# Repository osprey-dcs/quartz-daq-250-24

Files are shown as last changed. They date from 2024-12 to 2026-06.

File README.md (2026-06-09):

# Osprey Quartz DAQ-250-24

Open Hardware repository for Osprey DCS Quartz DAQ-250-24
distributed ADC chassis.

Revision 2

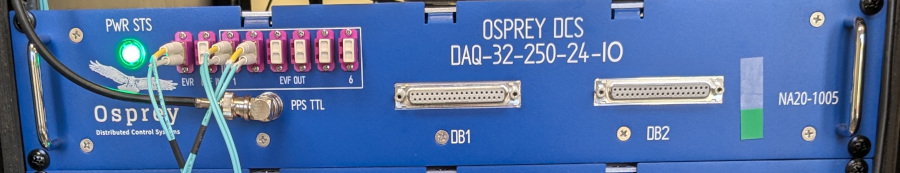
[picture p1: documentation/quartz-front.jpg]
Front panel


## Contents

- [3D model](chassis-rev2.stp.xz) of 2U Chassis, including Marble and Quartz PCBs
- [Bill of materials](chassis-bom-rev2.csv) for chassis assembly.
- [Wiring](chassis-wiring-rev2.kicad_sch) diagram.
- Pre-built [firmware](firmware) images

- Documents
  - Quartz [DAQ-250-24](documentation/quartz-daq-250-24-datasheet.md) datasheet
  - **[Quick-start](documentation/quick-start.md)** Guide
  - [EPICS IOC Setup](documentation/ioc-setup.md)
  - [Acquisition Engine](documentation/acquire.md) setup
  - New [System Setup](documentation/system-setup.md)
  - [Chassis Setup/Recovery](documentation/chassis-setup.md)
  - [New Marble PCB](documentation/marble-bring-up-procedure.pdf) one-time factory bring-up process
  - Quartz bench testing [report](documentation/functional-testing.md)
  - Notes for [RHEL](documentation/rhel-notes.md) derivatives
  - Quartz [file format](https://github.com/osprey-dcs/atf-previewer/blob/main/documentation/file-formats.md)

## Related

- [Marble PCB](https://github.com/BerkeleyLab/Marble) schematic and artwork
- [Marble MMC](https://github.com/BerkeleyLab/Marble-MMC) firmware
- [Marble bootloader](https://github.com/BerkeleyLab/Bedrock) firmware
  - [Alluvium](https://github.com/mdavidsaver/alluvium) remote flash chip access
- [Quartz PCB](https://github.com/osprey-dcs/Quartz) schematic and artwork
- [Quartz application](https://github.com/osprey-dcs/Quartz-firmware) firmware
- [Interlock I/O PCB](https://github.com/osprey-dcs/pmod-mps-io)

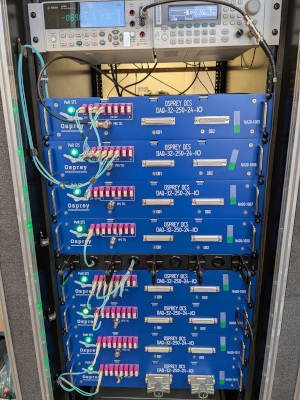
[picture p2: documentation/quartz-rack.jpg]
Installation


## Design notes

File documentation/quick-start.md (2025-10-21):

# Quartz Quickstart Guide

A (somewhat) quick overview of the components and processes for setting up a new Quartz ADC chassis.

## Equipment

* [Electrical](system-setup.md#prerequisites)
* Computing
  * Host for running GUI
  * Linux host for IOCs (no GUI).  May combine.
  * NTPv3 server (may use Linux host)
* Software processes
  * [Quartz IOC](ioc-setup.md#prerequisites) (required)
  * Control System Studio/Phoebus GUI client

## Preparation

* Install [Quartz IOC](ioc-setup.md#prerequisites) and associated software

## Physical

cf. [Single Chassis](system-setup.md#single-chassis) standalone wiring.

1. Unbox and rack up the Quartz chassis
1. Attach ground wire
1. Plug in 12V AC/DC power adapter
1. Connect ethernet
1. Connect pulse-per-second (PPS) input from GPS/GNSS (TTL).
1. [Connect micro-USB](chassis-setup.md#connect-usb) (optional, change IP configuration)

## IP address setup

Initially, the chassis should be directly connected (or on the same subnet)
as the computer used for

1. Apply power to chassis
1. Set [IP and/or MAC addresses](chassis-setup.md#set-ipmac-address)
1. Power cycle chassis
1. Ping test with new IP address
1. Boot chassis to [Application firewmare](ioc-setup.md#ioc-configuration).
   May be done with full IOC, or alluvium CLI.
1. Use Application console to set netmask and gateway.
   For node 1 (EVG) only, also set NTP server address
1. Power cycle or reboot

## Setup IOC

1. Build [Quartz IOC](ioc-setup.md#prerequisites) and dependencies.
1. Edit `iocBoot/iocNASA_ACQ/node01.cmd` with selected [correct IP address](ioc-setup.md#ioc-configuration), then run.
1. Check `FDAS:01:GLD:image` PV

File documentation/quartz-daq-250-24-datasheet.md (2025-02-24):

# Quartz DAQ-250-24 Datasheet

Osprey Quartz is a highly scalable EPICS native 24-bit 250KHz data acquisition system
consisting of one or more 2U 19-inch rack mounted chassis.
Each chassis can digitizer up to 32 channels connected through two standard DB37F connectors.
The input scale is fixed to $\pm 10$ volts with per-channel selectable AC or DC coupling.

Multiple chassis may be [connected together](system-setup.md#Topologies)
which maintaining a common sample clock phase.
This permits synchronous sampling with a very high channel count[^maxchan].

[^maxchan]: There is no hard upper limit on channel count.
  Sample clock synchronization quality degrades as timing network topology deepens.

## Parameters

| Parameter | Value |
| ---- | ---- |
| Height | 2U |
| Width | 19 Inch |
| Depth | 400 mm |
| Communication | 1Gbps Ethernet, RJ45 |
| Power Input Voltage | 12 VDC into 2 contact [DC barrel Jack](#PowerInput)[^acdc] |
| Number of Analog channels | 32 per chassis |
| Analog Input | 2x DB37-F |
| Sample rates | 1K, 5K, 10K, 25K, 50K, 250K samples per second |
| AC/DC coupling | selectable per-channel |
| ADC Resolution | 24-bit |

## Absolute Maximums

| Specification | Minimum | Maximum |
| ---- | ---- | ---- |
| Ambient Temperature | 0 C | 40 C |
| Ambient Humidity | | 90% non-condensing |
| Power Input Voltage[^acdc] | 0V DC | 13 VDC |
| Power Current | | 4A |
| Analog Input abs. voltage[^analogabs] | -15 V | +15 V (DC coupled) |
|                                       | -25 V | +25 V (AC coupled)[^analogabsac] |
| Analog Input diff. voltage[^analogdiff] | -30 V | +30 V |
| Pulse-per-second Input Voltage | -0.7 V | 5.5 V |

[^acdc]: 120V AC/DC converter included.
[^analogabs]: Voltage applied to any DB37 pin with respect to chassis ground.
[^analogabsac]: For frequencies less than the 16 Hz.
[^analogdiff]: Voltage difference between each pair of pins.

## Performance

| Specification | Minimum | Typical | Maximum |
| ---- | ---- | ---- | ---- |
| Power Input Voltage[^acdc] | 10 V | 12 V | 13 V DC |
| Analog Input Impedance | 999k ohm | 1M ohm | |
| Analog Input voltage | -10V | | 10V |
| Analog bandwidth | | | 100KHz @ 250Ksps|
|                  | | |  20KHz @ 50Ksps |
|                  | | |  10KHz @ 20Ksps |
|                  | | |  5KHz @ 10Ksps |
|                  | | |  2KHz @ 5Ksps |
|                  | | |  400Hz @ 1Ksps |
| Channel Cross-talk[^cross] | | | -94 dB |
| Gain Accuracy | | | 0.13 % |
| Pass-band ripple | 0.1 dB | | |
| Effective resolution | | 19 bits @ 250Ksps | |

[^cross]: Worst case of 100KHz measured on an adjacent channel on same side of PCB, sharing the same ADC chip.

## Connectors

- Power Input.

2 contact barrel jack, positive inside.  Cliff Electronics [SCD-026](http://www.farnell.com/datasheets/1859067.pdf)

- Grounding stud

- Ethernet RJ45 UTP

- Timing, 8x LC duplex, multi-mode

- 2x DB37-F

Each DB37-F connector has 16 inputs pairs.

Quartz DB37-F pinout

Board side connector is TE Connectivity [5747847-6](https://www.te.com/commerce/DocumentDelivery/DDEController?Action=showdoc&DocId=Catalog+Section%7F82068_AMPLIMITE_Right-Angle_Posted_Conn%7F0412%7Fpdf%7FEnglish%7FENG_CS_82068_AMPLIMITE_Right-Angle_Posted_Conn_0412.pdf%7F5747847-4)

- Pulse Per Second, BNC-F

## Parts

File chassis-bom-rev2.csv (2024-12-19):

QTY | Part | VENDOR | VENDOR# | Manufacturer | MFN# | Description | NOTE
1 | Fan extension cables | Amazon | Noctua NA-SEC2 | Noctua | NA-SEC2 | Pre terminated fan extension cables 12 in
1 | FGPA heatsink | Coolinnovations | 4-101010P | Coolinnovations | 4-101011P | Splayed Design, Copper Heat Sink | Use adhesive to attach to marble
2 | Fan guard | Digi-Key | 259-1623-ND | Sunon Fans | FG-4 | FAN GUARD 40MM METAL
2 | FAN1, FAN2 | Digi-Key | 259-1844-ND | Sunon Fans | MF40201V1-1000U-G99 | 12VDC Fan, 40 mm x 40 mm x 20mm
3 | Spades for LED+Fuse | Digi-Key | 314-AI-50207-ND | Mueller Electronics | AI-50207 | 0.250" (6.35mm) Quick Connect Female 18-22 AWG Crimp Connector Insulated
1 | Thermal Epoxy | Digi-Key | 473-8349TFM-50ML-ND | MG Chemicals | 8349TFM-50ML | Thermal Epoxy for heatsink | Adhesive for heatsinks
2 | BLK Hook Up Wire | Digi-Key | 5856/7BK005-ND | Alpha Wire | 5856/7 BK005 | HOOK-UP STRND 20AWG BLACK 100' | Wire for internal power
2 | RED Hook Up Wire | Digi-Key | 5856/7RD005-ND | Alpha Wire | 5856/7 RD005 | HOOK-UP STRND 20AWG RED 100' | Wire for internal power
1 | Crimp Tool (Power Connector) | Digi-Key | 58614-1-ND | TE Application Tooling | 58614-1 | TOOL HAND CRIMPER 18-24AWG SIDE
1 | Crimp Tool Die (Power Connector) | Digi-Key | A100343-ND | TE Application Tooling | 58614-2 | Tool Die Set For Rectangular Contacts, 18-24 AWG
2 | J19 Pins | Digi-Key | A19991CT-ND | TE Connectivity | 640252-2 | CONN SOCKET 18-24AWG CRIMP TIN
1 | J19 | Digi-Key | A24111-ND | TE Connectivity | 770849-2 | CONN RCPT HSG 2POS 3.96MM | Marble power connector
1 | SW1 | Digi-Key | EG1889-ND | E-Switch | RR3130ABLKBLKFS | SWITCH ROCKER SPST 10A 125V
1 | F1 | Digi-Key | F013-ND | Littlefuse | 03420838H | FUSE HLDR CART 250V 20A PNL MNT
1 | FUSE | Digi-Key | F1769-ND | Littelfuse Inc. | 0313005.MXP | FUSE GLASS 5A 250VAC 3AB 3AG
1 | Power Plug | Digi-Key | GSM60U12-P1J | Mean Well USA | 1866-5524-ND | AC/DC WALL MOUNT ADAPTER 12V 54W | Wall wort
2 | 2U Chassis Handles (comes with screws) | Digi-Key | HM1269-ND | Hammond Manufacturing | 1427Q | HANDLE STL/CHROME MTG CTR 2.299" | Handles
2 | JX-M1, JX-M2, 3 Pin Connector (Fan Cable) | Digi-Key | S9434-ND | Sullins Connector Solutions | SWH25X-NULC-S03-UU-BA | 3 Rectangular Connectors - Housings Receptacle Beige 0.100" (2.54mm) | Fan connector
6 | 3 Pin Connector Pins (Fan Cable) | Digi-Key | S9473TR-ND | Sullins Connector Solutions | SWT25X-URTC-S01-UU-UU | Socket Contact Tin 20-26 AWG Crimp - | Fan connector pins
1 | Ethernet | Digikey | 1195-3540-ND | HARTING | 9454521504 | CABLE MOD 8P8C JACK-PLUG 1.64'
1 | 12 VDC LED | Digikey | 350-4318-ND | Dialight | 655-1203-104F | LED PANEL INDICATOR GREEN 12V
1 | BNC to SMA Cable | Digikey | 3985-PE3733LF-12-ND | Pasternack | 3985-PE3733LF-12-ND | 12 inch BNC to SMA internal chassis cable
1 | Micro USB | Firewire | RR-MCBR-EXTPM-12GX5 | Firewire | RR-MCBR-EXTPM-12GX5 | Right angle micro usb cable
8 | LC Panelmount adapter | FS | FH-LCU-DXF-OM4 | FS | FH-LCU-DXF-OM4 | LC/UPC to LC/UPC Duplex OM4 Multimode SC Footprint Plastic Fiber Optic Adapter/Coupler with Flange
2 | SFP breakout cable | FS | FMTPLCOM4 | FS | FMTPLCOM4 | 1m (3ft) MTP® Female to 4 LC UPC Duplex 8 Fibers Type B Plenum (OFNP) OM4 50/125
2 | QSFP Adapater | FS | QSFP-SR4-40G | FS | QSFP-SR4-40G | Generic QSFP-SR4-40G Compatible 40GBASE-SR4 QSFP+
16 | nut for LC conenctors | McmasterCarr | 90592A075 | McmasterCarr | 90592A075 | Steel Hex Nut Class 8, M2 x 0.4 mm Thread | LC connector
8 | M4 Hex Nut, 100 Pack (fans) | McmasterCarr | 90710A035 | McmasterCarr | 90710A035 | 18-8 Stainless Steel Thin Hex Nut M4 x 0.7 mm Thread, DIN 439B, ISO 4035 | For fans
8 | Socket Head Screw M4 x 0.7 mm Thread, 30 mm Long (fans) | McmasterCarr | 91292A130 | McmasterCarr | 91292A130 | 18-8 Stainless Steel Socket Head Screw M4 x 0.7 mm Thread, 30 mm Long | For fans
16 | screw for LC connectors | McmasterCarr | 92000A017 | McmasterCarr | 92000A017 | Passivated 18-8 Stainless Steel Pan Head Phillips Screws M2 x 0.4mm Thread, 10mm Long | LC connector
15 | M2.5x0.45 Pan Head Phillips Screws (Marble+Quartz) | McmasterCarr | 92000A105 | McmasterCarr | 92000A105 | Passivated 18-8 Stainless Steel Pan Head Phillips Screws M2.5 x 0.45mm Thread, 8mm Long | Marble
16 | M4 Split Washer, 100 Pack (fans) | McmasterCarr | 92148A160 | McmasterCarr | 92148A160 | 18-8 Stainless Steel Split Lock Washer for M4 Screw Size, Standard, 4.4 mm ID | For fans
4 | Jack screw between Marble and Quartz | McmasterCarr | 93655A096 | McmasterCarr | 93655A096 | Male-Female Threaded Hex Standoff 4.500 mm Hex, 10 mm Long, M2.5 x 0.45 mm Thread
1 | Grounding wire | McmasterCarr | https://www.mcmaster.com/6981T6-6981T695/ | McmasterCarr | 6981T6 | Grounding wire to connect chassis to GND bar 500ft | GND
2 | Grounding lug | McmasterCarr | https://www.mcmaster.com/7113K455/ | McmasterCarr | 7113K455 | Ring terminal for GND 14-16 awg No10 screw | GND
1 | Grounding nut (chassis | McmasterCarr | https://www.mcmaster.com/91240A009/ | McmasterCarr | 91240A009 | 8-32 stainless steel nut | GND
1 | Grounding nut (GND bar) | McmasterCarr | https://www.mcmaster.com/91240A411/ | McmasterCarr | 91240A411 | 10-32 stainless steel nut | GND
1 | Grounding Screw | McmasterCarr | https://www.mcmaster.com/92597A140/ | McmasterCarr | 92597A140 | Grounding screw for GND bar 10-32 3/4in (pack of 25) | GND
3 | 19mm standoff for quartz | McmasterCarr | https://www.mcmaster.com/94868A173/ | McmasterCarr | 94868A173 | 19mm hex standoff 2.5M partially threaded | Quartz standoff
4 | Star washers | McmasterCarr | https://www.mcmaster.com/97775A521/ | McmasterCarr | 97775A521 | Star washers for grounding chassis and bar | GND
2 | 2.5M washers for Quartz standoffs | McmasterCarr | https://www.mcmaster.com/98689A111/ | McmasterCarr | 98689A111 | Pack of 100 2.5M washers | Quartz standoff
1 | BNC | Newark | 07H2407 | LCOM | BA1087 | Adapter Coaxial Connector BNC Jack, Female Socket To BNC Jack, Female Socket 50 Ohms
1 | PG1 | Newark | 94X0659 | Cliff Electronic Components | FC681445 | DC Power Connector, Jack, 2.1 mm, Panel Mount, Solder | Power plug
1 | Fan Filter | PPCS | MDY-FF-PVC-4 | PPCS | MDY-FF-PVC-4 | Ultra Thin 0.45mm PVC Fan Dust Filter - 4cm
1 | Marble Chassis | Protocase |  |  |  | 2U custom chassis frame built to house related components. Hardware Included. | Chassis Shell
16 | 8-32 countersunk screw | Protocase Supplied
16 | 8-32 PemNut | Protocase Supplied
6 | 8-32 stud | Protocase Supplied
6 | 8-32 nut | Protocase Supplied
12 | M2.5 PEM Standoffs 10mm | Protocase Supplied
2 | M2.5 PEM Stanoffs 19mm | Protocase Supplied
1 | Marble Board | Osprey DCS
1 | Quartz Board | Osprey DCS

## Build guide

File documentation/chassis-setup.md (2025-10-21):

# Quartz Chassis Setup and Recovery

This document describes a process to discover or set
the unique identifiers and firmware of a Quartz
digitizer chassis with unknown configuration.

This process consists of the following tasks:

1. Update application firmware
1. Set IP and MAC addresses
1. Completely reprogram flash chip (not recommended for end user)

## Prerequisites

1. Working Debian Linux 12 computer with internet access.
2. Quartz-DAQ-250-24 chassis
  - Marble 1.4.1 PCB
  - Quartz 1.x PCB (serial numbers less than 200)
3. Micro-USB cable
4. Fine point non-conductive stylus to operate micro-switch

## Preparation

```sh
# procedure tested with OpenOCD 0.12.0, pyserial 3.5
sudo apt-get install openocd python3-serial git

git clone https://github.com/mdavidsaver/alluvium.git
```

Download [marble.cfg](https://github.com/BerkeleyLab/Bedrock/blob/06b84d9ba8c3c41bc6aa823fadfbee9f15dfdd08/board_support/marblemini/marble.cfg#L2) or the [local copy](firmware/marble.cfg).

Download a [bootloader firmware](../firmware/marble-bootloader/) image file.

Download an [application firmware](../firmware/quartz-application/) image file.

## Program Application Firmware

The application firmware may be loaded while the bootloader firmware is running
via the alluvium utility.

```sh
$ cd alluvium
$ python3 -m alluvium 192.168.79.8 clear
$ python3 -m alluvium 192.168.79.8 erase app 8m
$ python3 -m alluvium 192.168.79.8 program app quartzV1-20241230-350d71f.bit
```

## Connect USB

Note: connecting the micro USB port will supply 3.3V power to an on-board FTDI USB to serial chip!
This may safely by done before or after connecting the main 12V power.
For the purposes of this document, connect the USB first in order to see output printed during MMC boot.

Depending on Quartz chassis revision, either plug into the front panel
USB port, or remove chassis lid and look for the USB pigtail port.

The micro USB connection on a Marble V1 PCB provides four virtual serial ports,
which will always appear in this relative order.

1. FPGA JTAG
2. Unused
3. FPGA debug UART
4. Management Microcontroller (MMC) UART

These will typically appear as `/dev/ttyUSB0` through `/dev/ttyUSB3`.
However, if eg. the host already has `/dev/ttyUSB0` for another device,
then they will appear as ttyUSB1 through ttyUSB3.
Assuming enumeration as 0 through 3, access the MMC console.

```sh
$ python -m serial.tools.miniterm /dev/ttyUSB3 115200
--- Miniterm on /dev/ttyUSB3  115200,8,N,1 ---
--- Quit: Ctrl+] | Menu: Ctrl+T | Help: Ctrl+T followed by Ctrl+H ---
```

Now switch on the chassis.  During the boot process the current
IP and MAC addresses will be printed.

## Set IP/MAC Address

The IP and MAC addresses may be changed via the MMC UART console.

While connected to the MMC UART, press `?` then Return to print a list of commands.

```
hardware board id 0x12

Build based on git commit 86a9bf22
Menu:
1 - MDIO/PHY
...
m d.d.d.d - Set IP Address
n d:d:d:d:d:d - Set MAC Address
...
```

The `m` and `n` commands will set/overwrite the addresses.

Quartz chassis are shipped with IP and MAC of the forms: `192.168.79.ddd` and `12:55:55:00:1f:XX`
where `ddd` and `XX` are the Marble PCB serial number in decimal and hexadecimal respectively.
eg. for Marble S/N 8.

```
m 192.168.79.8
n 12:55:55:00:1f:08
```

Note: there is no setting for network mask (netmask) or default gateway through the MMC console
as these are not necessary for LEEP traffic (device only replies to sender).
Network mask and gateway are separately configured for the Quartz application fireware,
for use by the NTP client.

### Verify Communication

After changing the IP address, power cycle the chassis and attempt to ping.

Note: the bootloader firmware will respond to a ping (ICMP), the application firmware will not.
      So for this test first stop any Quartz IOC from communication with the chassis.

Either firmware will respond to ARP requests.
So after attempting a `ping`, also check the ARP cache.

A positive result will show a MAC address (aka. Link Layer ADDRess):

```sh
$ ip neigh
...
192.168.79.7 dev eth0 lladdr 12:55:55:00:1f:07 REACHABLE
```

A negative result will not:

```sh
$ ip neigh
...
192.168.79.90 dev eth0 INCOMPLETE
```

The bootloader firmware may also be used with the `alluvium` tool.

```
$ cd alluvium
$ python3 -m alluvium 192.168.79.8 status
SR1 0b10011000 [SRWD  , p_err , e_err , BP2   , BP1   , bp0   , wel   , wip   ]
SR2 0b00000000 [es   , ps   ]
CR1 0b00100100 [lc1   , lc0   , TBPROT, dnu, bpnv  , TBPARM, quad  , freeze]
```

## Re-program Flash Chip

**Do not perform the following unless specifically directed to do so.**

## Overwrite FPGA bootloader image

As shipped, the 16MB flash chip on a Marble is partitioned into two 8MB sections
referred to as `gold` (lower) and `app` (upper).
The upper `app` section may be overwritten remotely at will.
The lower `gold` section is not writable without physical access to a chassis.

The following is **not necessary** to program the application image!

See for technical details on [flash chip write protections](https://github.com/mdavidsaver/alluvium/blob/master/marble-protect.md).

### Disable all flash write protections

1. Power off chassis
2. Toggle SW1 closed (tab towards QSFP cage)
3. Load the bootloader bit file into FPGA RAM

Run the following, replacing `/home/user/golden-1.4.1-b8ea502.bit` with the path
to the actual path to the file downloaded earlier.

Note: openocd does not expand tilda (`~`) in path names.

```sh
openocd -f marble.cfg -c 'transport select jtag; init; xc7_program xc7.tap; pld load 0 /home/user/golden-1.4.1-b8ea502.bit; exit'
```

Success exits with zero and output ends with

```
Info : JTAG tap: xc7.tap tap/device found: 0x0364c093 (mfg: 0x049 (Xilinx), part: 0x364c, ver: 0x0)
```

Unsuccessful has a non-zero exit code with an error like:

```
Error: couldn't stat() ~/golden-1.4.1-b8ea502.bit: No such file or directory
failed loading file ~/golden-1.4.1-b8ea502.bit to pld device 0
```

Also see the "libusb permissions" section below.

On success the FPGA is now running the golden/bootloader firmware,
which will be used to program the flash chip.

4. Zero the SR1 register

This step will fail unless SW1 is closed (see above)

```sh
python3 -m alluvium 192.168.79.8 clear
python3 -m alluvium 192.168.79.8 setup --sr1 0
```

Note: `clear` in this context clears flash chip error status,
      and does not alter the contents.

5. Optional, backup flash contents

```sh
# Optional
python3 -m alluvium 192.168.79.8 read 0 16M -f backup.bin
```

This backup may be restored with:

```sh
# Optional
python3 -m alluvium 192.168.79.8 program 0 backup.bin
```

6. Bulk erase

The following will erase the entire flash chip.

```sh
# Erases entire flash!!
python3 -m alluvium 192.168.79.8 wipe
```

7. Program bootloader firmware

Write the same firmware image file to the lower part of the flash.

```sh
python3 -m alluvium 192.168.79.8 program gold /home/user/golden-1.4.1-b8ea502.bit
```

8. Optional, verify

Power cycle the chassis and re-run:

```sh
python3 -m alluvium 192.168.79.8 clear
```

9. Restore write protections

```sh
python3 -m alluvium 192.168.79.8 clear
python3 -m alluvium 192.168.79.8 setup --sr1 0b10011000
```

10. Power off chassis
11. Toggle SW1 open (tab away from QSFP cage)

12. Optional, verify

The following commands will now fail.

```sh
python3 -m alluvium 192.168.79.8 setup --sr1 0

python3 -m alluvium 192.168.79.8 erase gold 8M
```

### libusb permissions

`openocd` errors like the following indicate that the user account does not have permission
to access the USB device.

```
Error: libusb_open() failed with LIBUSB_ERROR_ACCESS
Error: no device found
Error: unable to open ftdi device with vid 0403, pid 6011, description '*', serial '*' at bus location '*'
```

Either run as super-user or location change change
the permissions of the appropriate `/dev` file.

```sh
$ lsusb
Bus 001 Device 005: ID 0403:6011 Future Technology Devices International, Ltd FT4232H Quad HS USB-UART/FIFO IC
...
$ ls -l /dev/bus/usb/001/005
crw-rw---- 1 root plugdev 189, 4 Feb 15 08:39 /dev/bus/usb/001/005
$ sudo chmod a+rw /dev/bus/usb/001/005
```

## Quartz EEPROM

The Quartz PCB includes an EEPROM which holds FMC meta-data,
including manufacturer, product, and serial number in the
[FRU](https://www.intel.com/content/www/us/en/servers/ipmi/information-storage-definition.html)
(Field Replaceable Unit) format.

The [frugy](https://pypi.org/project/frugy/) tool can produce EEPROM images
using configuration files present in the
[Quartz](https://github.com/osprey-dcs/Quartz/tree/quartz-1.x/Documentation/EEPROM) repository.

```sh
sudo apt-get install python3-virtualenv atftp

git clone --branch quartz-1.x https://github.com/osprey-dcs/Quartz
cd Documentation/EEPROM

virtualenv /tmp/fruenv
. /tmp/fruenv/bin/activate
pip install frugy
```

Now create EEPROM image, and attempt to program and verify, serial number 256 (IP address `192.168.79.256`).

Substitute actual board variant and serial number.

```sh
./createEEPROM.sh QuartzEEPROM-v1.2.2.yml 256
```

When writing the EEPROM, the J6 jumper on Quartz must be **closed/shorted**.

The current contents may be read with:

```sh
atftp --get -l EEPROM_rb.bin -r FMC1_EEPROM.bin 192.168.79.256
```

And manually written confirmed with:

```sh
atftp --put -l EEPROM_010.bin -r FMC1_EEPROM.bin 192.168.79.256
atftp --get -l EEPROM_rb.bin -r FMC1_EEPROM.bin 192.168.79.256
diff EEPROM_010.bin EEPROM_rb.bin
```

It is strongly recommended to always read back and compare after writing to the EEPROM.

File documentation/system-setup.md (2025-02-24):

# Quartz ADC System Setup

This document describes setting up a new Quartz installation.

## Prerequisites

1. One or more Quartz ADC chassis
  - One 12V power supply for each
  - Ground connection (essential for measurement accuracy!)
2. Time server with 5V TTL PPS output
  - Either a dedicated ethernet enabled GPS receiver with NTP server
  - Another GPS receiver with 5V TTL PPS output, and a separate NTP server
3. Cables
  - cable to BNC-F on one Quartz chassis from time server (PPS)
  - LC duplex fiber patch cables
    - At least one is required to test a single chassis
  - Ethernet cable(s) to computer
4. Working Debian Linux 12 computer with internet access.

## EVG / Timing Master Node

In each installation, one chassis must be selected as a "master" node for the timing network.
This node will connect to the time server via. ethernet and pulse-per-second inputs and
provide timing and synchronization for all other chassis.

Any chassis may act as a "master" node.
This selection is made by configuring the NTP server through the
[application firmware console](ioc-setup.md#fpga-application-console).

### Time Server Setup

For production installations, a dedicated time server with GPS input, NTP server, and PPS output is recommended.

Alternately, for testing and development, the following parts may be assembled to provided a suitable
PPS, along with a software NTP server.

- [GPS GNSS with USB](https://www.adafruit.com/product/4279)
- [SMA to uFL adapter](https://www.adafruit.com/product/851)
- [GPS Antenna - External Active](https://www.adafruit.com/product/960)
- [BNC Male Plug Terminal Block](https://www.adafruit.com/product/2888)
- Suitable wire, soldering iron, and a steady hand.

## Connections

Summary of Quartz chassis connectors referenced below

- Fiber (LC)
  - Port 1 - EVR IN
  - Port 2 - EVG IN
  - Ports 3 -> 8 - EVF OUT
- PPS TTL (BNC)

## Topologies

### Single chassis

The minimal connections required to run a single chassis are:

- Port 3 -> Port 1
- Time server PPS output -> PPS TTL
- Ethernet connection between chassis, computer, and NTP server

Single chassis

### Up to 6 chassis

Up to 5 more chassis may be connected from Ports 4 through 8 on the "master" node
to EVR IN on each secondary node.

Six chassis

### 7 to 32 chassis

With more than six chassis, it is necessary to add tertiary (level 3) nodes from
one or more secondary (level 2) nodes.

32 chassis

Here each Level 2 node will connect to itself, and up to 5 other Level 3 nodes.

This arrangement require an alteration to the "master" node, which will no longer
be looped directly to itself.
Instead, the "master" node will be connected to itself through one of the level 2 nodes.

This maintains an equal propagation time from from the Ports 3 -> 8 on the "master"
node, and the Port 1's on each node (including the master).

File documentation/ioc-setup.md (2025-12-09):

# Quartz EPICS IOC Setup

This document describes setting up and running an EPICS IOC
to communicate with a Quartz ADC chassis

## Prerequisites

1. Working Debian Linux 12 computer with internet access.
2. Quartz-DAQ-250-24 chassis
  - IP address known.
  - This document uses `192.168.79.8` as an example
  - Application firmware image programmed
3. (Optional) Installation of cs-studio phoebus GUI

## Preparation

```sh
sudo apt-get update
sudo apt-get install -y build-essential git libevent-dev libz-dev libfftw3-dev libreadline-dev python3 python3-serial python-is-python3
```

```sh
git clone --branch 7.0 https://github.com/epics-base/epics-base
git clone --branch master https://github.com/epics-base/pvxs
git clone --branch master https://github.com/epics-modules/autosave
git clone --branch master https://github.com/osprey-dcs/feed-core
git clone --branch master https://github.com/osprey-dcs/pscdrv
git clone --branch main https://github.com/osprey-dcs/atf-acq-ioc
git clone https://github.com/mdavidsaver/alluvium

cat <<EOF > pvxs/configure/RELEASE.local
EPICS_BASE=\$(TOP)/../epics-base
EOF

cat <<EOF > autosave/configure/RELEASE.local
EPICS_BASE=\$(TOP)/../epics-base
EOF

cat <<EOF > feed-core/configure/RELEASE.local
EPICS_BASE=\$(TOP)/../epics-base
EOF

cat <<EOF > pscdrv/configure/RELEASE.local
EPICS_BASE=\$(TOP)/../epics-base
EOF

cat <<EOF > pscdrv/configure/CONFIG_SITE.local
USE_FFTW=YES
EOF

cat <<EOF > atf-acq-ioc/configure/RELEASE.local
AUTOSAVE=\$(TOP)/../autosave
PVXS=\$(TOP)/../pvxs
FEED=\$(TOP)/../feed-core
PSCDRV=\$(TOP)/../pscdrv
EPICS_BASE=\$(TOP)/../epics-base
EOF

make -C epics-base
make -C autosave
make -C pvxs
make -C feed-core
make -C pscdrv
make -C atf-acq-ioc
```

## IOC configuration

```sh
cd atf-acq-ioc/iocBoot/siocNASA_ACQ
```

Edit for example `node01.cmd` and change the value of `NASA_ACQ_BASE_IP` to eg. `192.168.79.8`.

Then run:

```sh
./node01.cmd
```

In another terminate run:

```sh
$ export PATH="$PATH:$PWD/epics-base/bin/linux-x86_64"

$ caget -S FDAS:01:GLD:image FDAS:01:GLD:FW_CODEHASH FDAS:01:APP:FW_CODEHASH
FDAS:01:GLD:image              Gold
FDAS:01:GLD:FW_CODEHASH b8ea50264fe8ccb7195b3ff14c909a2c56b085a0
FDAS:01:APP:FW_CODEHASH
```

A value of `Gold` should be shown to indicate that the IOC is communicating with the bootloader firmware.

A value of `None` indicates lack of communication.  Stop and troubleshoot.

Now boot to the application image, this may take ~30 seconds.

```sh
$ caput FDAS:01:GLD:boot 0
Old : FDAS:01:GLD:boot               Boot
New : FDAS:01:GLD:boot               Boot
```

```sh
$ caget -S FDAS:01:GLD:image FDAS:01:GLD:FW_CODEHASH FDAS:01:APP:FW_CODEHASH
FDAS:01:GLD:image              Appl
FDAS:01:GLD:FW_CODEHASH
FDAS:01:APP:FW_CODEHASH 19d434014ec88c9652fc332fa56cfe995219bbe4
```

### Alternative boot

The alluvium tool can be used to boot to the application firmware separately from the IOC.

```sh
$ python3 -m alluvium 192.168.79.8 clear
SR1 0b10011000 [SRWD  , p_err , e_err , BP2   , BP1   , bp0   , wel   , wip   ]
SR2 0b00000000 [es   , ps   ]
CR1 0b00100100 [lc1   , lc0   , TBPROT, dnu, bpnv  , TBPARM, quad  , freeze]
$ python3 -m alluvium 192.168.79.8 reboot app
```

## FPGA Application Console

The `atf-acq-ioc/scripts/console.py` script allows communication with
the application firmware expert console.
Currently this access is only necessary to configure a chassis as a timing "master" (EVG) node.

Application firmware must be running.

```sh
./atf-acq-ioc/scripts/console.py -a 192.168.79.8
```

Note: Issue `Ctrl+c` to interrupt the script.

Initially issue the `log` or `help` command to check communication.
(type the command then press Return)

The startup log output will look like:

```
log
Firmware build date: 1737417442
Software build date: 1737416340
JEDEC ID: 01 20 18
Flash SR:98 CR:24
Block protection set (SR:98).ASPR: FE7F
First DYBAR: FF
Microcontroller:
  U28: 39.5 C
  U29: 41.0 C
  Firmware: 86A9BF22
  MAC address: 12:55:55:00:1F:07
 IPv4 address: 192.168.79.7
 IPv4 netmask: 255.255.255.0
 IPv4 gateway: 192.168.79.1
 IPv4 NTP server: 192.168.79.99
FMC1 EEPROM at 0x54:
   Manufacturer: Osprey
           Name: Quartz
  Serial Number: 202
    Part Number: v2.1.1
Boot flash write protected.
```

Query current IP configuration

```
gw
 IPv4 netmask: 255.255.255.0
 IPv4 gateway: 192.168.79.1
ntp
 IPv4 NTP server: 192.168.79.99
```

Use the `gw` and `ntp` commands configure the NTP server address (**node 1/EVG only**),
netmask, and default gateway.

For a EVG node:

```
ntp 192.168.79.99 255.255.255.0
```

For all other nodes:

```
ntp 0.0.0.0 255.255.255.0
```

To clear issue `ntp 0.0.0.0`.
If the netmask is omitted, then `255.255.255.0` is used.
Acknowledge and reboot (power cycle or issue `boot` command)

When configured as a master/EVG, the node will attempt to contact the NTP server on startup.
Success looks like:

```
NTP round trip 6123341 us
Time 1739846200:3258402 after 408 us
```

Failure looks like:

```
Warning -- No response from NTP server.
```

**The master/EVG node must synchronize with the NTP server prior to any acquisition.**

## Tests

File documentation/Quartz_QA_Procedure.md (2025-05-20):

# Quartz Quality Assurance Procedure
## Purpose
The purpose of this document is to have a consistent unified way each Quartz Board is tested before deployment. This procedure will be updated periodically to improve QA of the boards.

## Equipment needed
* Stanford Research Systems DS360 Low Distortion Generator
* 2 x BNC to DB37 Cable (BNC to All channels)
* BNCs to DB37 Cable (BNC to Individual Channel)
* Multimeter (Fluke 115 or better)
* Triple output Benchtop Power Supply 
* 2 x FMC Power breakout module [link](https://www.iamelectronic.com/shop/produkt/fpga-mezzanine-card-fmc-power-module/)
* Marble Testing Chassis
* PC to run IOC and Phoebus

## Procedure
### Visual Inspection
Check visual for any board defects. If the board has come back from rework look at the reworked areas carefully under magnification for any shorts etc.

Areas to check with extra scrutiny are around the ADC chips, around the Relays, the clocking distribution components.

<div align="center"><b>Record in Testing Log when complete</b></div>

***

### Power Testing
Next the Board will be powered up in various ways to protect other testing hardware.

***

### Looking for Shorts to GND
Using the multimeter check that all voltage
[test points](https://github.com/osprey-dcs/Quartz/blob/quartz-1.x/Documentation/Quartz%20Test%20Points.pdf)
have a resistance to board ground greater than 1kΩ.

| Test Point Reference | SilkscreenedLabel | Nominal Voltage |
| ---- | ---- | ---- |
| TP 1 | P1_2P5V | +2.5V  |
| TP 2 | P2_2P5V | +2.5V  |
| TP 3 | +5V | +5V  |
| TP 4 | +3.3V | +3.3V  |
| TP 5 | +16V | +16V  |
| TP 6 | +15V | +15V  |
| TP 7 | -15V | -15V  |
| TP 8 | -16V | -16V  |
| TP 9 | GND | 0V  |
| TP 10 | GND | 0V  |
| TP 11 | +12V | +12V  |

<div align="center"><b>Record in Testing Log when complete</b></div>

***

### 12V/3.3V/2.5V Power Testing
One at a time inject 12V,3.3V & 2.5V using the voltage test points found on the board. Do this with a 1.5A current limit.

Note variance from nominal current if found.

Nominal expected current draw is:
<table border="1"; style="border-collapse: collapse;">
    <tbody>
        <tr><td>12V</td><td>~850mA</td></tr>
        <tr><td>3.3V</td><td>&lt;100mA</td></tr>
        <tr><td>2.5V</td><td>&lt;100mA</td></tr>
    </tbody>
</table>

<div align="center"><b>Record in Testing Log when complete</b></div>

***

### FMC breakout Power Testing
Using a 3 output power supply and two FMC Power breakout modules: Power up all input power rails (12V/3.3V/2.5V) simultaneously

Note variance from nominal current if found.

Nominal expected current draw is:
<table border="1"; style="border-collapse: collapse;">
    <tbody>
        <tr><td>12V</td><td>~850mA</td></tr>
        <tr><td>3.3V</td><td>&lt;100mA</td></tr>
        <tr><td>2.5V</td><td>&lt;100mA</td></tr>
    </tbody>
</table>

<div align="center"><b>Record in Testing Log when complete</b></div>

***

### Power up with Marble
Attach a now power tested quartz to a **powered off** marble testing chassis.

Power up the testing chassis.

Start the IOC.

Ensure proper readback of diagnostic quartz signal (voltage, etc.).

<div align="center"><b>Record in Testing Log when complete</b></div>

***

### EEPROM Programmed

According to the [Quartz EEPROM](https://github.com/osprey-dcs/quartz-daq-250-24/blob/master/documentation/chassis-setup.md#quartz-eeprom) programming guide,
checkout the branch/revision appropriate to the PCB model to be programmed,
and edit `createEEPROMs.sh` with the appropriate serial numbers.

For the Quartz version 1 PCBs delivered, use the `quartz-1.x` branch.

<div align="center"><b>Record in Testing Log when complete</b></div>

***

### Signal Check All DC
Until mentioned otherwise, connect the DS360 Low Distortion Generator output (with output disabled) to a tee then to two BNC to DB37 Cables (BNC to All channels). Connect the two DB37 ends to the Quartz Inputs.
* Set Data Acquisition to 250kHz sampling in Phoebus
* Set all Channels to DC input coupling
* Run the following signals into all channels simultaneously
* +/-10V amplitude sine wave at 10kHz
* +/-9V with a +0.5V DC offset amplitude sine wave at 10kHz
* 0V

Look at real-time min/max/average/std. deviation results of all channels while injecting these signals and look for any outliers or anomalous readings or high noise.

<div align="center"><b>Record in Testing Log when complete</b>
</div>

***

### Signal Check All AC
* Set Data Acquisition to 250kHz sampling in Phoebus
* Set all Channels to AC input coupling
* Run the following signals into all channels simultaneously
    * +/-10V amplitude sine wave at 10kHz
    * +/-9V with a +0.5V DC offset amplitude sine wave at 10kHz
    * 0V

Look at real-time min/max/average/std. deviation results of all channels while injecting these signals and look for any outliers or anomalous readings.

<div align="center"><b>Record in Testing Log when complete</b></div>

***

### Toggle Channels to DC
* Set Data Acquisition to 250kHz sampling in Phoebus
* Set all Channels to **AC input coupling**; should already be their if following along
* Run the following signal into all channels simultaneously
    * +/-9V with a +0.5V DC offset amplitude sine wave at 10kHz
* Toggle each channel to DC mode one at a time and observe the 0.5V offset appearing in the real time readback data.

<div align="center"><b>Record in Testing Log when complete</b>
</div>

***

### Toggle Channels to AC
* Set Data Acquisition to 250kHz sampling in Phoebus
* Set all Channels to DC input coupling
* Run the following signal into all channels simultaneously
    * +/-9V with a +0.5V DC offset amplitude sine wave at 10kHz
* Toggle each channel to AC mode one at a time and observe the 0.5V offset disappearing in the real time readback data.

<div align="center"><b>Record in Testing Log when complete</b></div>

***

### Test at All frequencies
* Set all Channels to **DC input coupling**
* Run the following signal into all channels simultaneously
    * +/-9V with a +0.5V DC offset amplitude; log sine wave sweep from 100Hz to 100kHz @ 0.2Hz rate
* Set Data Acquisition to 250kHz sampling in Phoebus
* Look at FFT of channels for anomalous results
##
* Set Data Acquisition to 50kHz sampling in Phoebus
* Change sweep to 100Hz to 25kHz @ 0.2Hz rate
* Look at FFT of channels for anomalous results
##
* Set Data Acquisition to 25kHz sampling in Phoebus
* Change sweep to 100Hz to 13kHz @ 0.2Hz rate
* Look at FFT of channels for anomalous results
##
* Set Data Acquisition to 5kHz sampling in Phoebus
* Change sweep to 50Hz to 3kHz @ 0.2Hz rate
* Look at FFT of channels for anomalous results
##
* Set Data Acquisition to 1kHz sampling in Phoebus
* Change sweep to 10Hz to 500Hz @ 0.2Hz rate
* Look at FFT of channels for anomalous results
##

<div align="center"><b>Record in Testing Log when complete</b>
</div>

***

### Crosstalk Check
* Note - This test should be complete for at least two PCBs for any newly manufactured batch
* Disable the DS360 Low Distortion Generator output.
* Replace testing cables with the BNCs to DB37 Cable (BNC to Individual Channel)
* Inject a +/-10V amplitude; log sine wave sweep from 100Hz to 100kHz @ 0.2Hz rate in 4 random channels one at a time (1 random channel on each of the board’s ADC)
* Look to see that other channels are below ~56e-6 times lower than the channel with signal.
    * Note any channels above the expected nominal 15e-6 times (~ -95dB) level 

<div align="center"><b>Record in Testing Log when complete</b>
</div>

***

## Start/Completion Validation

Record the git commit of **this QA procedure** in the Testing Log.

Also record the following:
<br>
Tests Performed By: _________________
<br>
Date Initiated: ______________________
<br>
Date Completed: ____________________
<br>
Finally indicate a Pass/Fail if this performed with no deviations or waivers

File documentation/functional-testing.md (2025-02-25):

# Quartz Design Functional Testing

Updated: 24 Feb. 2025

## Linearity Testing

### Test setup

A Stanford Research Systems DS360 is used to generate a test signal. This signal is injected into all signal channels through DB37 testing cable.  
Unless otherwise noted testing parameters are as follows:

- Input into all channels  
- Board is set to 250kHz sampling.  
- Channels set to DC coupling  
- Amplitude of the test signal is stepped in 1V increments across the \+/-10V (20Vp-p) full listed input range

### Testing Results

Below is the plot showing all channels data while running the test.  
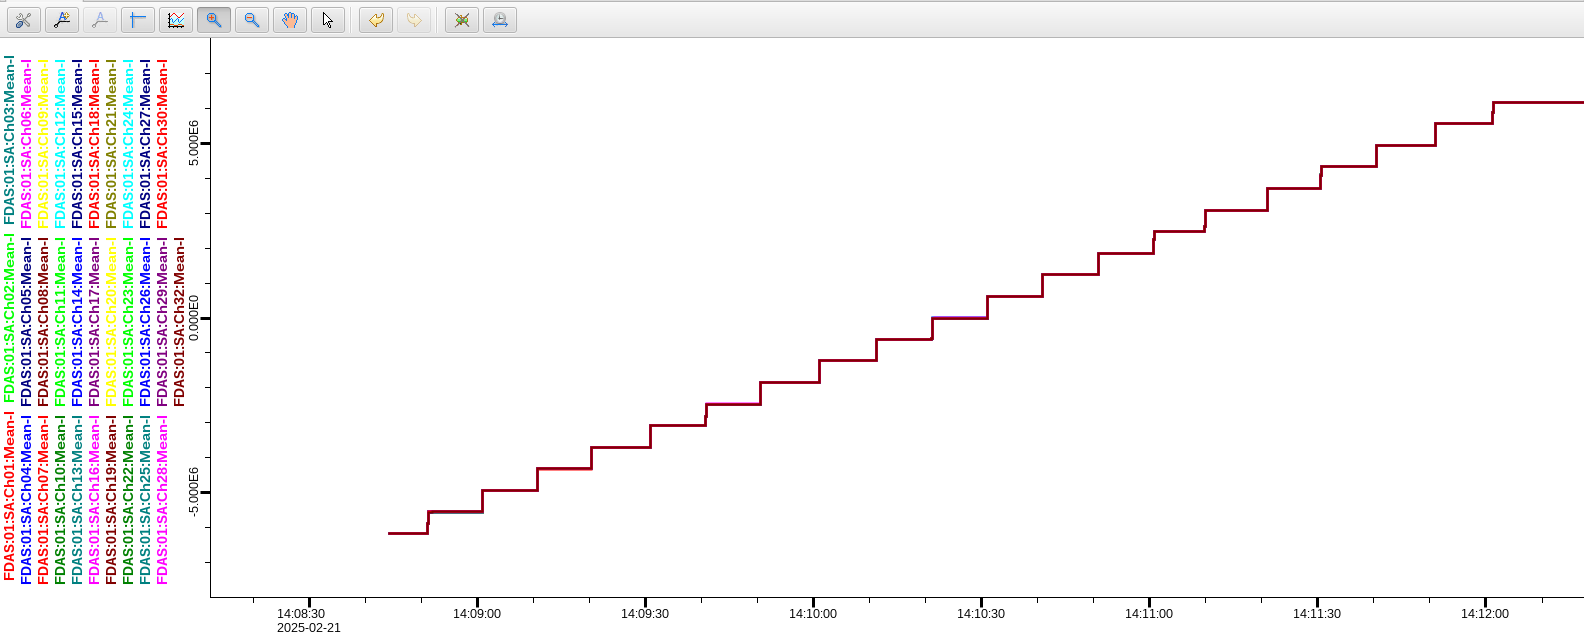
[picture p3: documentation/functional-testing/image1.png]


The DC voltage was stepped from \-10V through 10V at approximately 10 sec intervals. This gave \~250 million samples per step of data.  
The data was then analyzed to give an upper bound of linearity. The sample with the largest variance from the ideal count was collected and shown in the table linked below.  
[google sheet link](https://docs.google.com/spreadsheets/d/1LSDJu8C6iC6pIeCDivs3sl-keTuAOCS9q5x6OPSTIlo/edit?usp=sharing)

Without gain or zero calibration applied the upper bound on linearity for these 32 channels are below

| Channel 1 | 0.1189% | Channel 17 | 0.1253% |
| :---- | ----: | :---- | ----: |
| Channel 2 | 0.1227% | Channel 18 | 0.1257% |
| Channel 3 | 0.1252% | Channel 19 | 0.1262% |
| Channel 4 | 0.1233% | Channel 20 | 0.1258% |
| Channel 5 | 0.1207% | Channel 21 | 0.1257% |
| Channel 6 | 0.1199% | Channel 22 | 0.1261% |
| Channel 7 | 0.1158% | Channel 23 | 0.1262% |
| Channel 8 | 0.1161% | Channel 24 | 0.1259% |
| Channel 9 | 0.1179% | Channel 25 | 0.1264% |
| Channel 10 | 0.1199% | Channel 26 | 0.1267% |
| Channel 11 | 0.1205% | Channel 27 | 0.1272% |
| Channel 12 | 0.1216% | Channel 28 | 0.1281% |
| Channel 13 | 0.1226% | Channel 29 | 0.1281% |
| Channel 14 | 0.1235% | Channel 30 | 0.1284% |
| Channel 15 | 0.1242% | Channel 31 | 0.1228% |
| Channel 16 | 0.1244% | Channel 32 | 0.1286% |

After applying a gain or zero calibration, the upper bound on linearity for these 32 channels are below

| Channel 1 | 0.0822% | Channel 17 | 0.0829% |
| :---- | ----: | :---- | ----: |
| Channel 2 | 0.0824% | Channel 18 | 0.0830% |
| Channel 3 | 0.0826% | Channel 19 | 0.0832% |
| Channel 4 | 0.0823% | Channel 20 | 0.0832% |
| Channel 5 | 0.0822% | Channel 21 | 0.0833% |
| Channel 6 | 0.0822% | Channel 22 | 0.0835% |
| Channel 7 | 0.0820% | Channel 23 | 0.0836% |
| Channel 8 | 0.0820% | Channel 24 | 0.0836% |
| Channel 9 | 0.0821% | Channel 25 | 0.0838% |
| Channel 10 | 0.0823% | Channel 26 | 0.0840% |
| Channel 11 | 0.0823% | Channel 27 | 0.0842% |
| Channel 12 | 0.0824% | Channel 28 | 0.0845% |
| Channel 13 | 0.0825% | Channel 29 | 0.0845% |
| Channel 14 | 0.0826% | Channel 30 | 0.0847% |
| Channel 15 | 0.0827% | Channel 31 | 0.0848% |
| Channel 16 | 0.0828% | Channel 32 | 0.0849% |

### Conclusion

It has been shown that an upper bound of linearity of the quartz design well exceeds the goal of 1%.  
It must also be pointed out that the test signal used only had an accuracy tolerance of 1%. This was not corrected for in the above analysis, pointing to the nominal linearity being better than the upper-bound  figures shown above.

## Crosstalk Testing

### Test setup

A Stanford Research Systems DS360 is used to generate a test signal. This signal is injected into a signal channel through DB37 breakout cable, while the other channels are shorted.  
Unless otherwise noted testing parameters are as follows:

- Input into channel 17 (centered in the board)  
  - No appreciable difference affecting conclusion on choosing another channel.  
- Board is set to 250kHz sampling.  
- Channels set to DC coupling  
- Amplitude of the test signal is set to \+/-10V (20Vp-p) representing the full listed input range

### Testing Results

Testing shows some crosstalk is noticeable between 10kHz-100kHz. Below 10kHz potential crosstalk is within the observed noise floor. Crosstalk is observed on physically adjacent channels that share the same digitizing ADC. Little to no crosstalk is seen on adject channels on a separate ADC.

Sweeping frequency from 100Hz to 100kHz over 10 seconds  
Channel 17 (channel with signal input):  
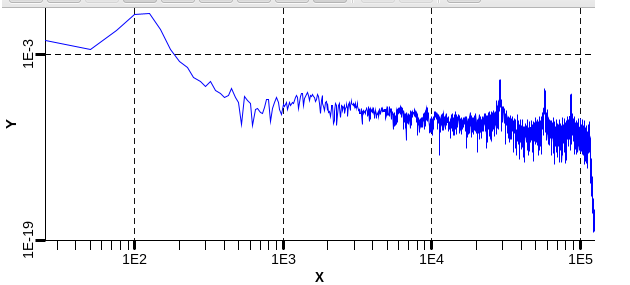
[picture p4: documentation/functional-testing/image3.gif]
  
Channel 18 (Adjacent Channel sharing ADC):  
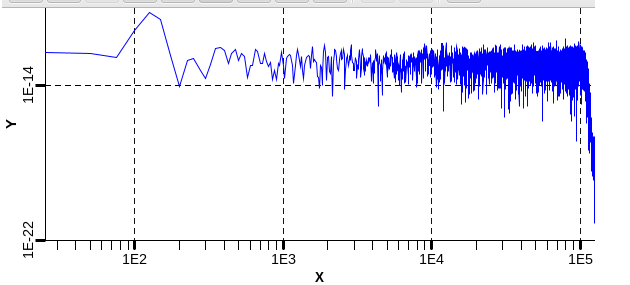
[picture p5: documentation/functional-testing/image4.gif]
  
Channel 16 (Adjacent Channel not sharing ADC):  
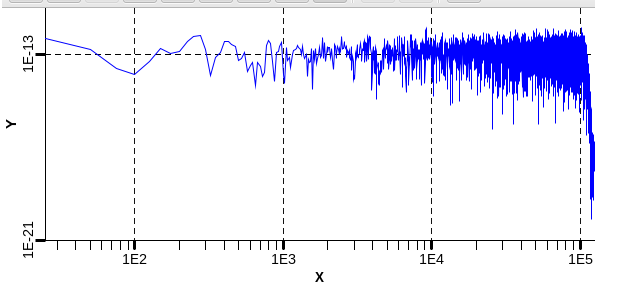
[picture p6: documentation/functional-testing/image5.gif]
  
The following is some plots showing the worst case observed crosstalk  
FFT PLOT of input @99.9kHz  
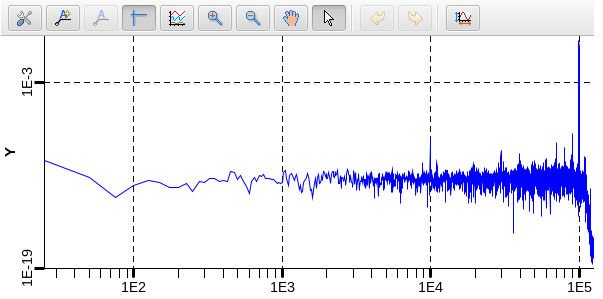
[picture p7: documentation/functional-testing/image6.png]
  
FFT PLOT of adjacent channels @99.9kHz
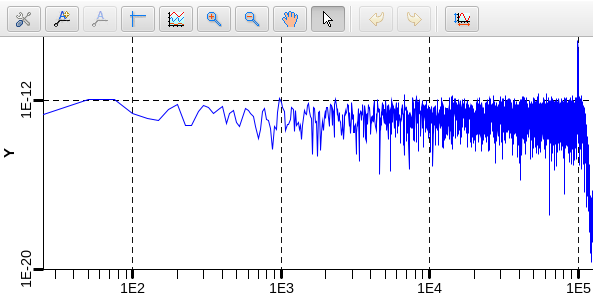
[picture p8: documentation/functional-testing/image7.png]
    

Below is a plot displaying the relative magnitude of the cross alk between the input channel and some adjunct channels.The input was a single tone starting at 100kHz and then stepping down by 10kHz every few seconds down to 10kHz.  
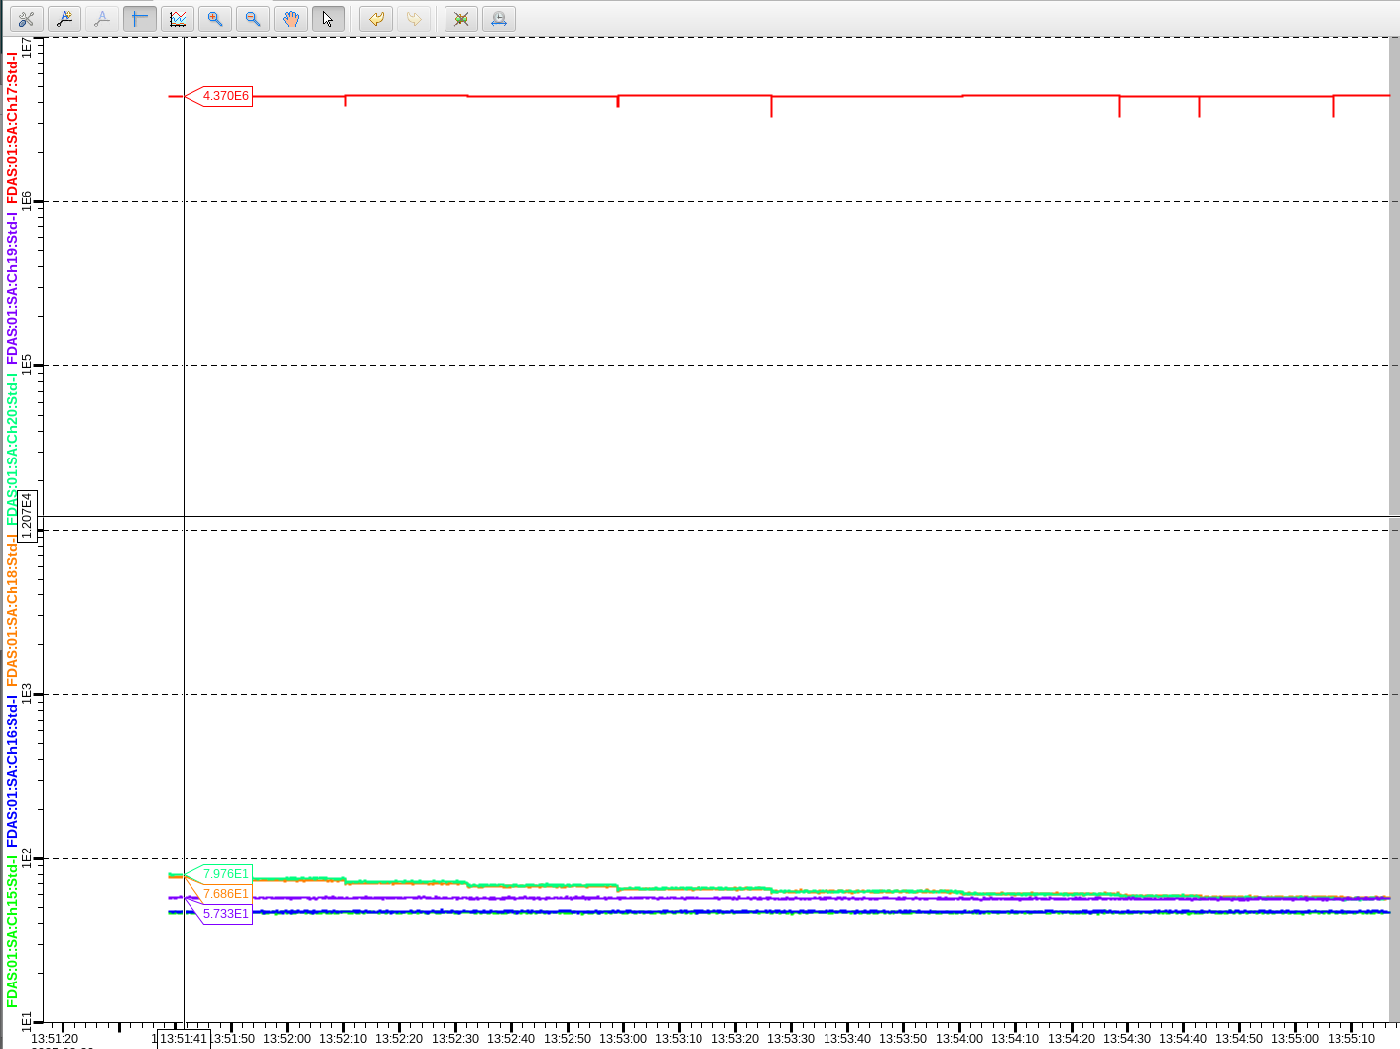
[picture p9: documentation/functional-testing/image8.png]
  
The upper red trace is showing the magnitude of the channel where input is present  
You can see there are 3 bands of channel magnitudes.  
The upper of these bands are adjacent channels on the same ADC.  
The middle band are channels on the sma ADC but on the opposite side of the board  
The lower band are other channels not sharing an ADC with the input channel.

Below is a table of results showing the worst case ratio seen at each of the sample rates

| frequency | input magnitude | crosstalk magnitude | ratio of crosstalk to input | crosstalk (dB) |
| :---- | ----- | ----- | ----- | ----- |
| 100 kHz | 4369600 | 80.42 | 54334.74 | \-94.702 |
| 90 kHz | 4349997 | 76.65 | 56751.43 | \-95.080 |
| 80 kHz | 4373394 | 73.20 | 59745.82 | \-95.526 |
| 70 kHz | 4358293 | 68.71 | 63430.26 | \-96.046 |
| 60 kHz | 4374473 | 65.18 | 67113.73 | \-96.536 |
| 50 kHz | 4363253 | 63.63 | 68572.26 | \-96.723 |
| 40 kHz | 4372892 | 61.26 | 71382.50 | \-97.072 |
| 30 kHz | 4333453 | 59.49 | 72843.39 | \-97.248 |
| 20 kHz | 4367424 | 58.75 | 74339.13 | \-97.424 |
| 10 kHz | 4381942 | 58.13 | 75381.77 | \-97.545 |

Next a sweep is performed from 1Hz to 2kHz over 10 seconds, using 25kHz sampling  
Ch17  
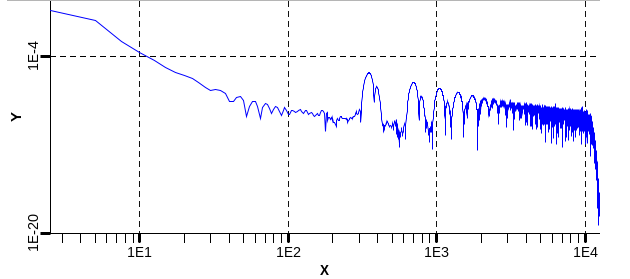
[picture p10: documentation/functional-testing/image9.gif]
  
Ch18  
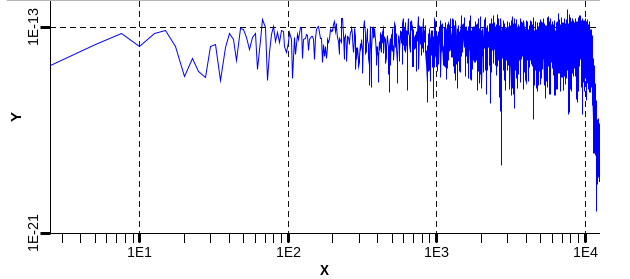
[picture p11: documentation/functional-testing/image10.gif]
  
Measurement of crosstalk while running this sweep is at or better than 105dB, which isn’t discernible from any other non-input channel. The measurement is limited the board’s noise floor

### Conclusion

Our design greatly exceeds the F2.8 specification of less than \-80 dB DC to 2 kHz of crosstalk. Even when looking at the full bandwidth of the system we don’t encroach on this requirement.

## Alias Rejection Testing

### Test setup

A Stanford Research Systems DS360 is used to generate a test signal. This signal is injected into all signal channels through DB37 testing cable.  
Unless otherwise noted testing parameters are as follows:

- Input into all channels  
- Channels set to DC coupling  
- Board is set to 250kHz sampling.  
- Amplitude of the test signal is set to \+/-10V (20Vp-p) representing the full listed input range

### Testing Results

The easiest way to show the effectiveness of the built-in antialias filter of the ADC is to sweep the input frequency up to the sample frequency and look for reflections in the FFT. Below are such plots at each of the 4 higher sample rates

FFT of 100Hz \- 250kHz linear sweep over 10 seconds @ 250kHz sampling  
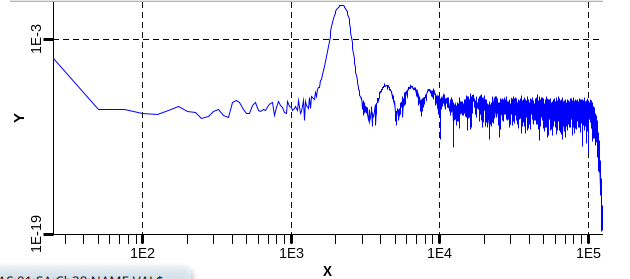
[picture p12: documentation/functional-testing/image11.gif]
   
FFT of 100Hz \- 50kHz linear sweep over 10 seconds @ 50kHz sampling  
    
FFT of 100Hz \- 25kHz linear sweep over 10 seconds @ 25kHz sampling  
  
FFT of 10Hz \- 5kHz linear sweep over 25 seconds @ 5kHz sampling  
  

### Conclusion

Our design does not exhibit aliasing when frequencies beyond that Nyquist frequency of a sample rate are present. The built-in antialias filter of the ADC is appropriately functioning.  
See Antialiasing Section on page 63 of the AD7768 datasheet \[[link](https://www.analog.com/media/en/technical-documentation/data-sheets/ad7768-7768-4.pdf)\]

## 

## AC/DC Switching Testing

### Test setup

A Stanford Research Systems DS360 is used to generate a test signal. This signal is injected into all signal channels through DB37 testing cable.  
Unless otherwise noted testing parameters are as follows:

- Input into all channels  
- Board is set to 250kHz sampling.  
- Amplitude of the test signal is set to \+/-10V (20Vp-p) representing the full listed input range

### Testing Results

This will be tested by starting channel input in DC coupling mode with a 500Hz \+/-10V (20Vp-p) with a 5V DC offset. This will show clear signs of clipping as the signal will be outside the listed input range. The AC/DC coupling will be then toggled and we will immediately see the clipping disappear.  


### Conclusion

The AC/DC coupling functionality is fully working as expected in the design.
